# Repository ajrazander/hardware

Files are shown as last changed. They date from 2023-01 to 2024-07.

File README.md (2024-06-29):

# Hardware
Fun designs demonstrating cool aspects of trapped ion quantum computing.

# [How to trap an atom](https://github.com/ajrazander/hardware/tree/main/ion-trap-demo)

Spinning saddle trapped a ping pong ball

This physics demo shows how an individual atom can be "trapped" for experimental study using an [Paul trap](https://en.wikipedia.org/wiki/Trapped_ion_quantum_computer#Paul_trap). State-of-the-art Paul traps are used for [trapped-ion quantum computers](https://en.wikipedia.org/wiki/Trapped_ion_quantum_computer) and [mass spectroscopy](https://en.wikipedia.org/wiki/Quadrupole_ion_trap). This demo is intended to be as inexpensive as possible (including some 3D printed parts).

### Instructions
Read the [build instructions](https://github.com/ajrazander/hardware/blob/main/ion-trap-demo/README.md#build-instructions) for how to assemble the pieces together including some pictures and videos of it working.

### Experiments
Read the [experiments section](https://github.com/ajrazander/hardware/tree/main/ion-trap-demo#experimenting) for ideas to get you thinking and learning.

# [Hands on Qubit](https://github.com/ajrazander/hardware/tree/main/bloch-sphere-demo)

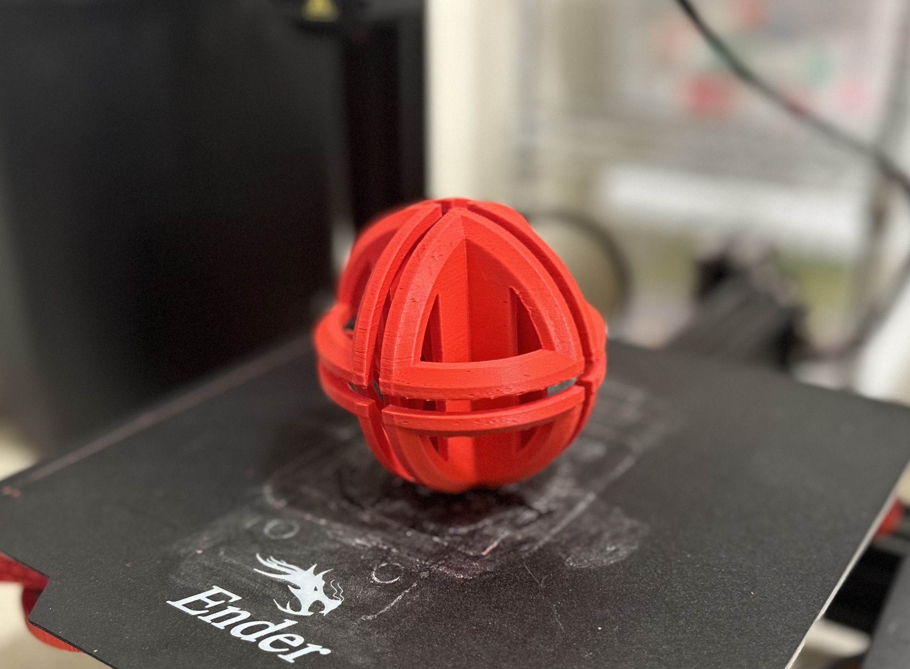
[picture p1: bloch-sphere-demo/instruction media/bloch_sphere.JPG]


Hold a quantum bit---[a qubit](https://en.wikipedia.org/wiki/Qubit)---in your hands and recreate modern experiments with this fully 3D printable [Bloch sphere](https://en.wikipedia.org/wiki/Bloch_sphere) and qubit state vector.

### Instructions
[Read the build instructions](https://github.com/ajrazander/hardware/tree/main/bloch-sphere-demo/README.md#build-instructions) for stl files and assembly.

### Experiments
Coming....

# Want to use these?
I'm happy to see this work be used and shared, so please contact me and request permission before using any of the designs above per the licensing agreement.

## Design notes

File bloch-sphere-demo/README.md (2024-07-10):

# The Bloch Sphere
The [Bloch sphere](https://en.wikipedia.org/wiki/Bloch_sphere) is a visual representation of a two-level quantum system---aka a [qubit](https://en.wikipedia.org/wiki/Qubit). In experiments, qubits do not physically look like the Bloch sphere, but the Bloch sphere can describe the dynamics of a single qubit. Here, you'll have a hands-on learning experience to learn the quantum physics behind qubits, and various techniques used in modern day experiments.

# Build Instructions

### Parts list
* Bloch sphere. A 3D printed Bloch sphere where the qubit vector can glide along set rails. (see designs/bloch_sphere.stl). (June 2024)
* Qubit vector. A 3D printed qubit vector that glides along the Bloch sphere rails. (see designs/qubit_vector.stl) (June 2024)

### Designs
The designs folder holds the 3D printed components which you will need to print:
1. The Bloch sphere. Print with supports.
2. The qubit vector. Printable without supports.

### Assembly

1. Print Bloch sphere (requires supports). Remove support material. Consider sanding where supports were.



2. Print qubit vector.

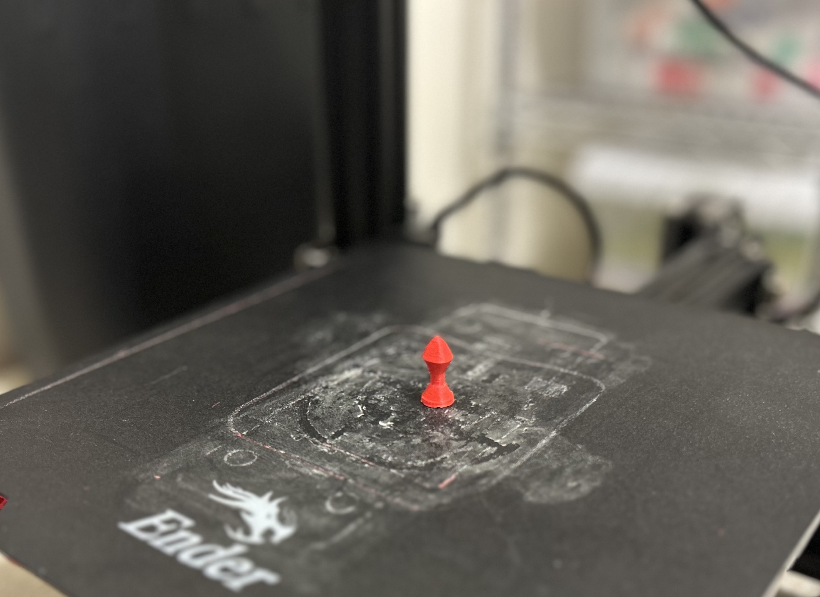
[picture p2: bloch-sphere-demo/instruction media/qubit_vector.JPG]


3. Slip qubit vector into Bloch sphere rails. It’s easiest at an intersection.

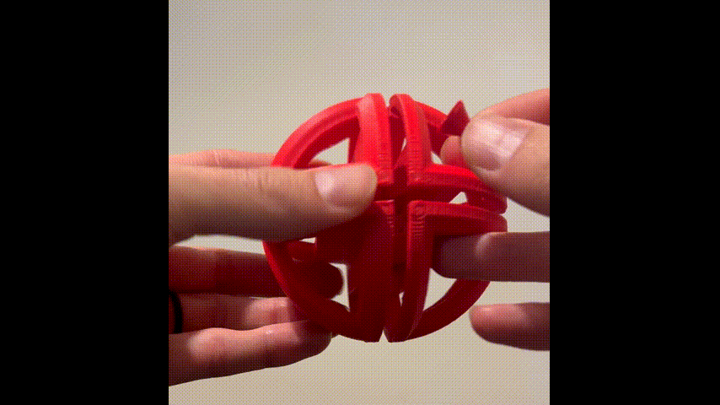
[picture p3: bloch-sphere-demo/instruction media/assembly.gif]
Slip qubit vector into Bloch sphere rail


#  Experimenting
Coming…

### Noncommuting quantum operations

Rubik's cube demonstration. The cube is rotated two different directions. Depending on the order, the yellow side ends up in a different location.

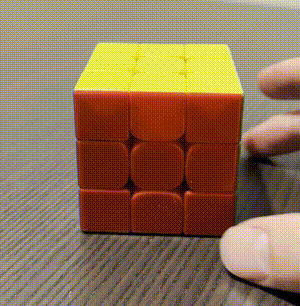
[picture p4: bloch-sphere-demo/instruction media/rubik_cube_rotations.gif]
Rotations on Rubik's cube


Bloch sphere demonstration. The vector is rotated two different directions. Depending on the order, the vector ends up in a different location. This is an example of how the order of quantum operations also matter.

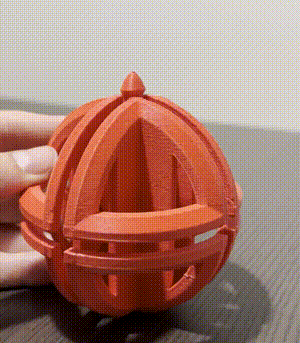
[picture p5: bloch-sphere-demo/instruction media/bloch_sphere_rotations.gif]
Rotations on the Bloch Sphere


# Literature
Coming...

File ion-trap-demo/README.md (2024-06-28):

# The Trapped Atomic Ion
How do you trap one atom? Wolfgang Paul and Hans Dehmelt were awarded [the Nobel Prize](https://www.nobelprize.org/prizes/physics/1989/summary/) for one strategy which is now called [the Paul trap](https://en.wikipedia.org/wiki/Ion_trap) (or RF trap). Here, you'll demonstrate it with a ping pong ball for the ion (a charged atom) and a spinning saddle for the oscillating voltages.

Spinning saddle trapped a ping pong ball

The physics of how an *individual* atom can be "trapped" in a vacuum for experimental study is fascinating. It's also led to a few Noble prizes and dramatically advanced the fields of [atomic, optical, and molecular physics](https://en.wikipedia.org/wiki/Atomic,_molecular,_and_optical_physics) as well as [quantum information](https://en.wikipedia.org/wiki/Quantum_information). This ion trap demo is a simple analogy for how individual atoms are actually trapped in a [linear Paul trap](https://en.wikipedia.org/wiki/Ion_trap#Linear_Paul_Trap).

In Paul traps used for quantum computing, the atom would first be ionized by a laser (or two) at the center of the Paul trap. The atom then has a net positive charge, so we call it an ion. The ion's net charge is pushed by the voltages on the Paul trap's electrodes in such a way that the ion can't escape--hence the ion is "trappped". How the electrode voltages can push on the ion is actually quite limited (see [Earnshaw's theorem](https://en.wikipedia.org/wiki/Earnshaw%27s_theorem)). To get around this limitation, Paul trap electrodes have oscillating (colloquially refered to as rf) voltages and static voltages. *We'll just focus on the oscillating voltages in this demo.* The oscillating voltages make a saddle like shape, but why doesn't the ion just fall off the sides of the saddle and escape? This demo shows how. Gravity and the rotating saddle simulate how the oscillating voltages in a linear Paul trap can trap an ion.

# Build Instructions

### Parts list
This is what and where I purchased each item (if you find something cheaper let me know).
* Housing. A 3D printed container to hold everything together (see designs/box_v4.stl). (Feb 2023)
* Saddle potential. A 3D printed saddle that "traps" the ping pong ball (see designs/saddle_100xy_50z.stl). (Jan 2023)
* ~600 grit sand paper. You want something fine to smooth the saddle. This will dramatically increase the trapping time. (Jan 2023)
* 12V DC motor (you'll want it geared down to the range of a few hundred RPM). Used to spin the saddle. Review the paper under the literature folder to calculate how much speed you may want. 1Hz (60 RPM) seems to be a golden speed for most saddles. I purchased one [online for $15](https://www.amazon.com/gp/product/B072R5G5GR/ref=ppx_yo_dt_b_asin_title_o08_s00?ie=UTF8&th=1) that's probably too beefy but I like the standing geometry (Jan 2023).
* 12V DC motor speed controller. You could make this yourself if you have access to a basic electronics. I purchased [these online for $10](https://www.amazon.com/gp/product/B08HQQR3FQ/ref=ppx_yo_dt_b_asin_title_o01_s01?ie=UTF8&psc=1) (Jan 2023)
* 8 AA battery holder. Used to power the DC motor. I bought it [here for $7](https://www.amazon.com/gp/product/B07WP1CYYW/ref=ppx_yo_dt_b_asin_title_o01_s00?ie=UTF8&psc=1) (Jan 2023)
* 8 AA batteries. (Jan 2023)
* Ping pong ball. The ping pong ball is the "atom" in the trap. I used a standard 40mm size ping pong ball and [purchased a few here for $10](https://www.amazon.com/gp/product/B00V57KP1G/ref=ppx_yo_dt_b_asin_title_o00_s00?ie=UTF8&th=1). (Jan 2023)
* 2 wires. You'll need 2 wires (red and black look cool) to go from the controller to the motor. (Jan 2023)

### Designs
The designs folder holds the 3D printed components which you will need to print:
1. The saddle which sits on top of the motor shaft.
2. The housing that holds all the components together.
The Mathematica file "saddle-design.nb" allows you to export your own custom saddle stl file. (It's suprisingly easy; then use tinkercad to get the DC motor attachment shaft on the saddle).

### Assembly
Order and 3D print the parts. On the speed controller PCB board, secure wire leads that will go to the battery holder and the DC motor (see step 3 for better image).

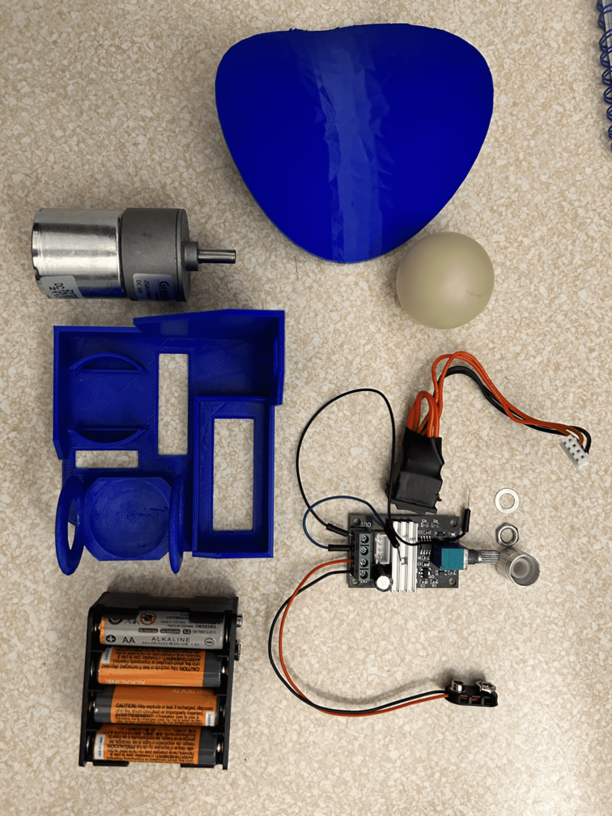
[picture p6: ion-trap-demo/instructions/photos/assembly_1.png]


1. Place batteries in the battery holder and wiggle it into its slot on the 3D printed housing. It should fit snuggly.

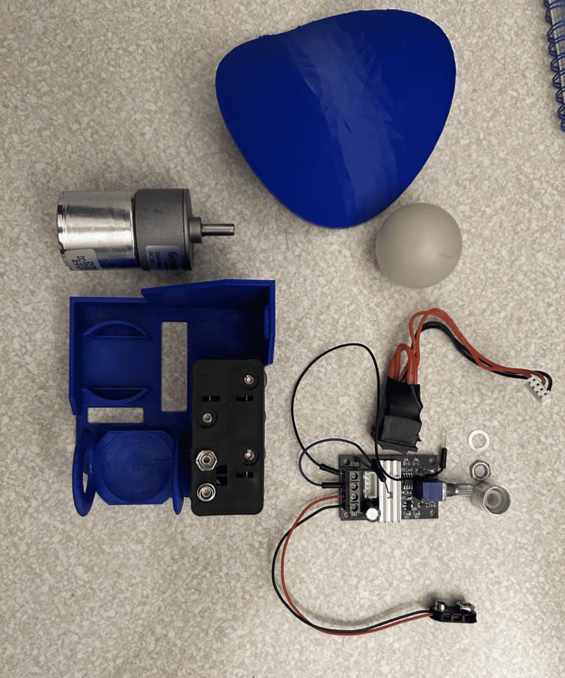
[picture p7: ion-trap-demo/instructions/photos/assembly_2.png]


2. Attach the speed controller board to the 3D printed housing. Disconnect the speed controller’s black switch. Pull the outer knob off the potentiometer and take off the washer and nut under the knob. Push the exposed potentiometer knob through the bottom hole of the 3D printed housing (see image below). This might need some moderate force and wiggling to get the threads through the hole. Reassemble the knob: put the washer back on, tighten the nut, and push the knob back on.

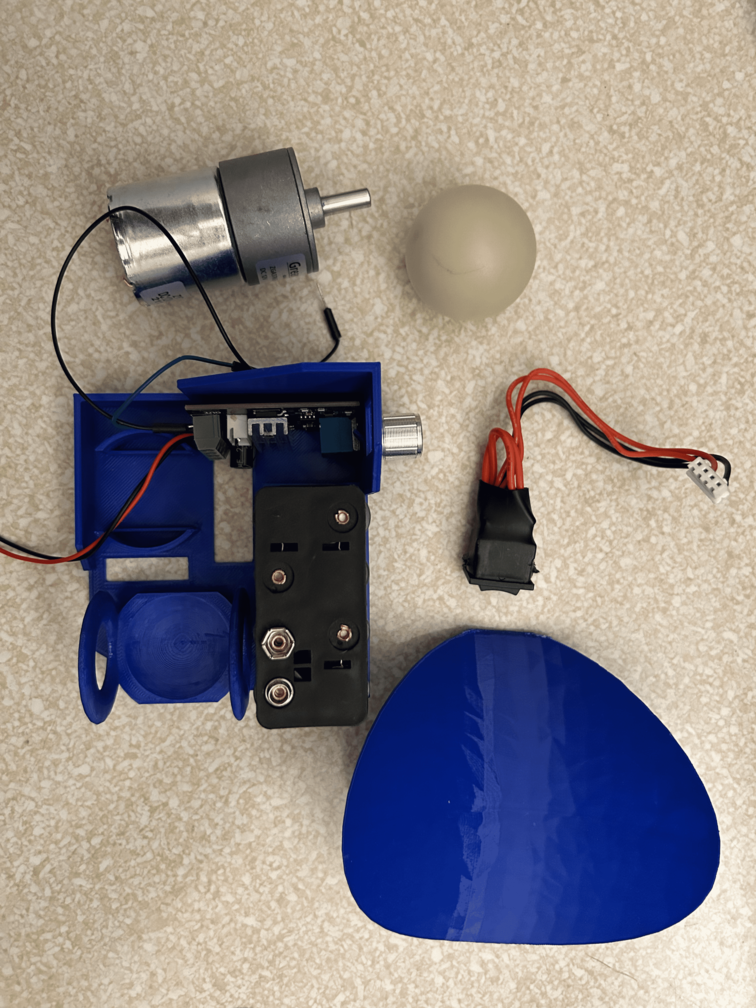
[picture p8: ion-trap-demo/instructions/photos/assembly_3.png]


3. Attach the speed controller power output to the DC motor. It doesn’t matter which lead from the speed controller is connected to the plus or minus lead of the DC motor. Definitely use a more secure connection than shown here (such as soldering on the wires).

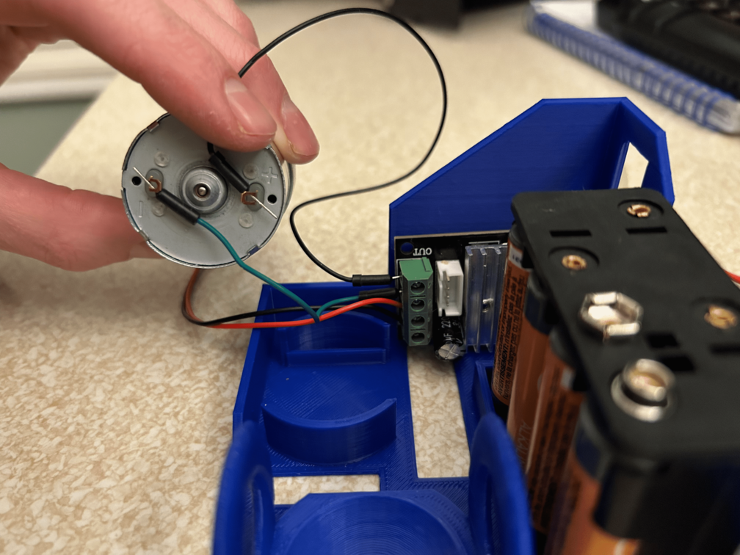
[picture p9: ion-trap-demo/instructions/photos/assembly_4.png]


4. Put the DC motor in the cylindrical base. Be sure the 3D printed parallel rails in the cylinder match with the metal groves at the bottom of the DC motor casing. This stabilizers the motor’s rotation. Confirm the fit by wiggling the DC motor. It should not rotate.

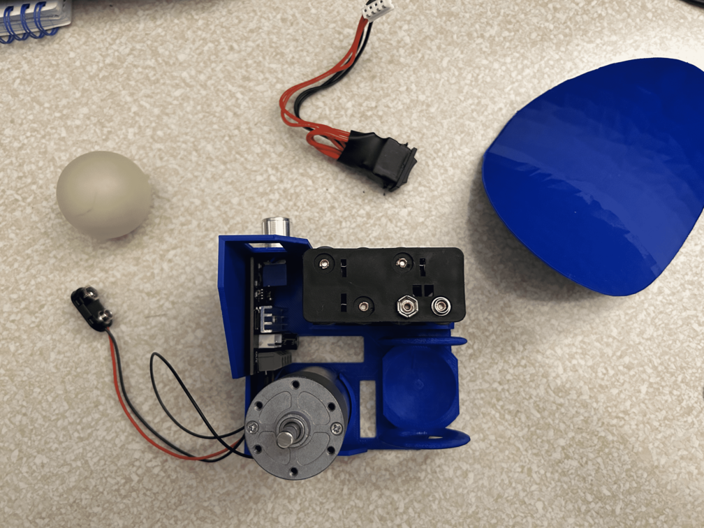
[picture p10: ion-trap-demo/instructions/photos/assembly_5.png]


5. Attach the speed controller switch. Push the white plug from the front rectangular hole of the 3D printed housing to inside the housing by the speed controller. Plug it in to the speed controller. Carefully wiggle and push the black switch into place. It will be a tight fit.

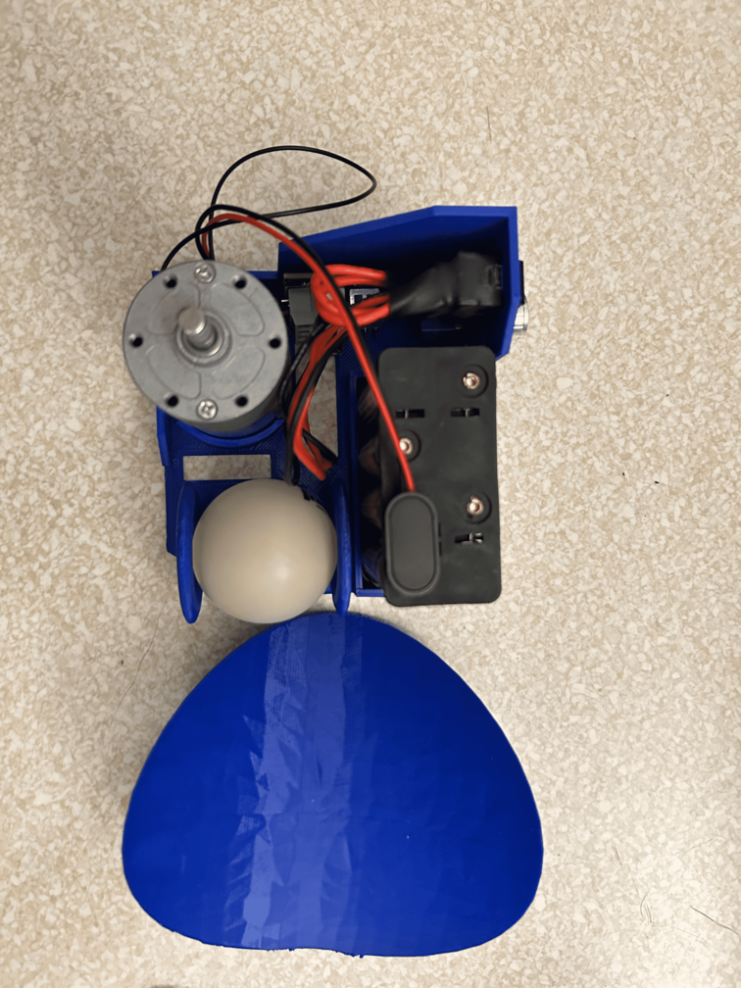
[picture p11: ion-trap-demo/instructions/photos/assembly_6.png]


6. Wrap up. With the speed controller’s switch off. Attach the battery wire leads to the battery holder. Slip the ping pong ball into the socket. Find the flat side of the DC motor shaft and the flat side of the 3D printed saddle’s base and push the saddle on. This might need a bit of force, but should slide on nicely.

7. **You will need to smooth the 3D printed saddle to get good trapped times** (~ minutes of trapping are possible with very smooth saddles). Read more about this under Experimenting point 3.

#  Experimenting
1. Test the DC motor is working as expected. Turn on the dc motor using the controller (without the saddle on the DC motor shaft). Does the DC motor shaft spin? Is the DC motor stable in the cylindrical base? Does varying the speed controller’s potentiometer knob affect the DC motor’s speed? Can you get to the rotational speed you want/calculated for the saddle shape you 3D printed? Troubleshoot accordingly ;).

2. Measure the affect of the saddle’s speed on the trapping time. Start with the saddle spinning at slow speed. Place the ping pong ball in the center of the spinning saddle. If it rolls off, try increasing the speed. If the saddle looks like its flinging the ping pong ball off, try decreasing the speed. Measure the saddle rotation speed and the trapping time. Make a plot.

3. Measure the affect of friction on the trapping time. Measure how long you can keep the ping pong ball trapped in the saddle with different smoothness. Without smoothing the 3D printed saddle, I get about ~10 seconds. After 15 minutes of moderately sanding with wet 600 grit sand paper, I get ~30 seconds. With another 15 minutes of more aggressive sanding (wet sand paper and buff it with a rag so I can’t feel any bumps with my fingers), I can get 60 seconds. Doing more smoothing and adding a dry lubricant (such as non-stick Teflon spray), I’ve seen 10 minutes of continuous trapping.

3. How does the initial condition of the ping pong ball affect the trapping time? Try comparing on-center with off-center starting positions. Try placing the ball in the saddle vs giving the ball a little spin. Try spinning the ping pong ball with vs against the saddle direction. What happens? 

4. Try different balls and saddle shapes! (See designs folder for the Mathematica notebook that can export new saddle stl files)

5. And of course, what’s the longest trapping time you can get and what helped the ball stay trapped for so long?

# Literature
Contains papers I found useful when designing this project as well as the physics this demo is demonstrating. Here are some nice youtube videos demonstrating or explaning the physics in no particular order:
* https://youtu.be/9TH5mFHLmfc
* https://youtu.be/1NBOsELakx4

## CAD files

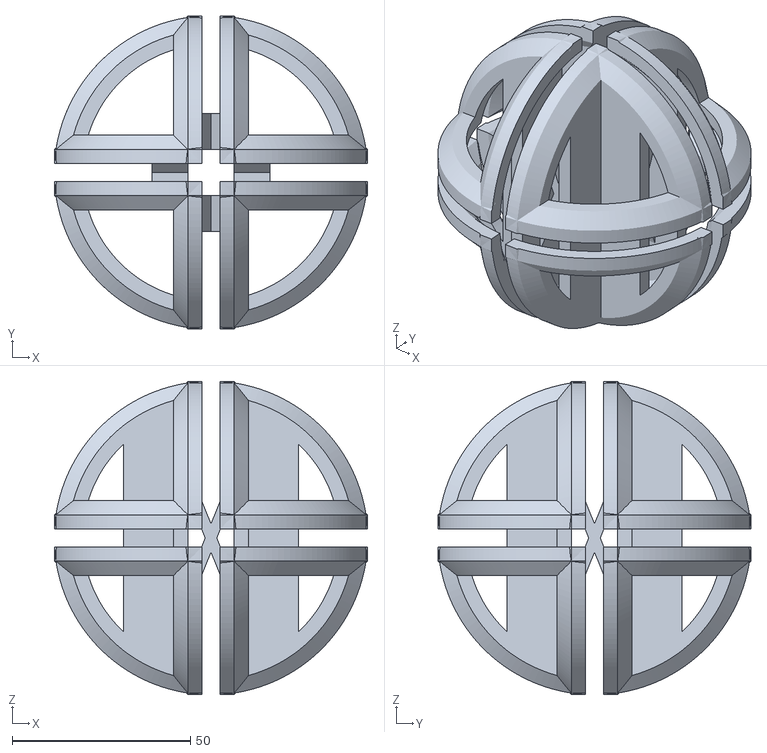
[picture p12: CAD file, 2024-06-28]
bloch-sphere-demo/designs/bloch_sphere.stl
87.9 x 87.9 x 87.9

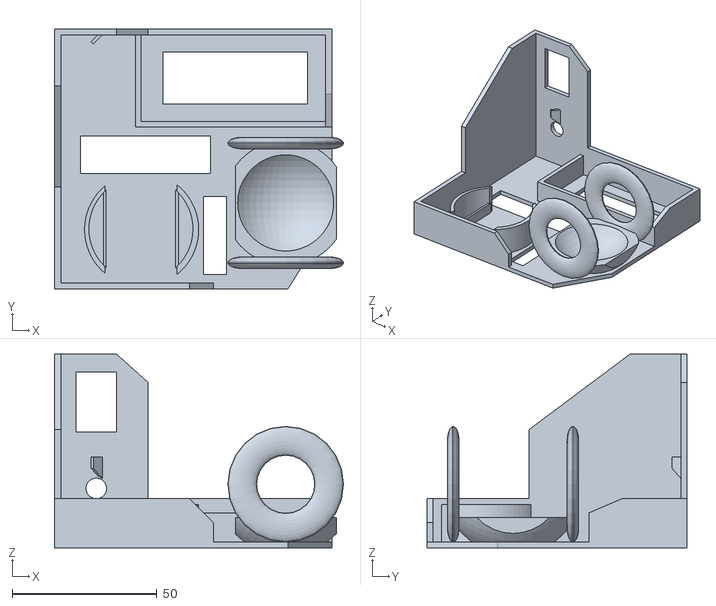
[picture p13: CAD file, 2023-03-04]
ion-trap-demo/designs/box_v4.stl
100.0 x 90.0 x 67.0

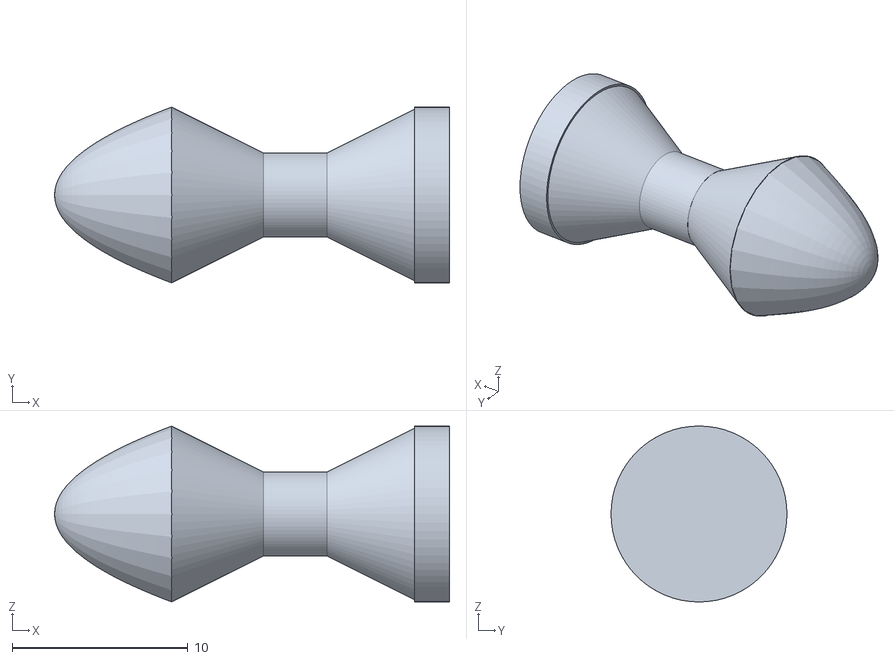
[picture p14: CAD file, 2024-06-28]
bloch-sphere-demo/designs/qubit_vector.stl
22.5 x 10.0 x 10.0

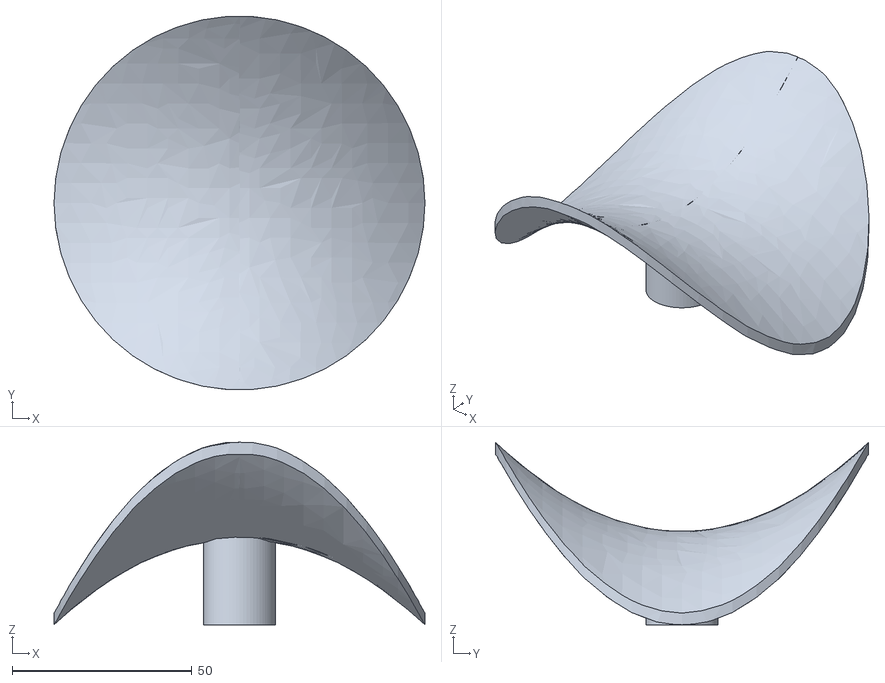
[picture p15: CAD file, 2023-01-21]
ion-trap-demo/designs/saddle_100xy_50z.stl
103.3 x 103.9 x 50.8

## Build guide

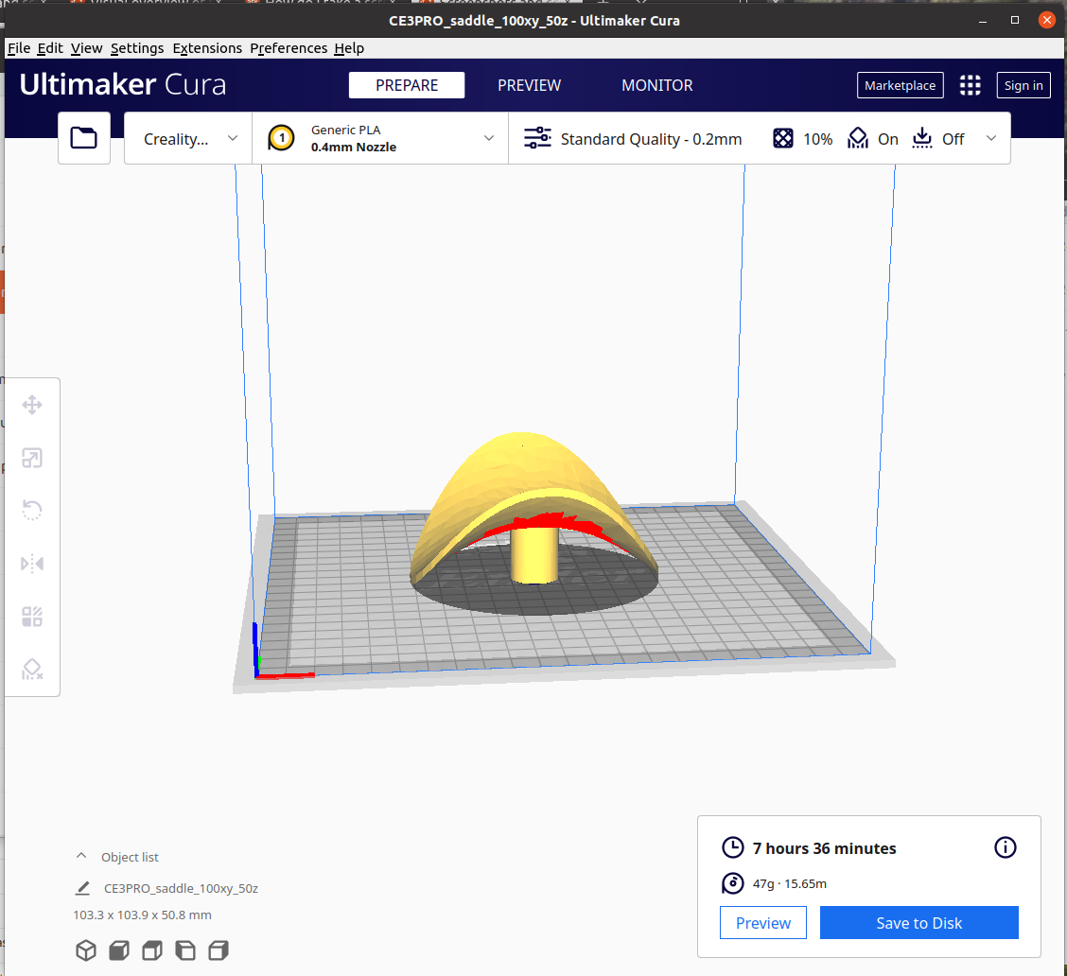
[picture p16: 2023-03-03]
ion-trap-demo/instructions/photos/imported_stl_saddle.png

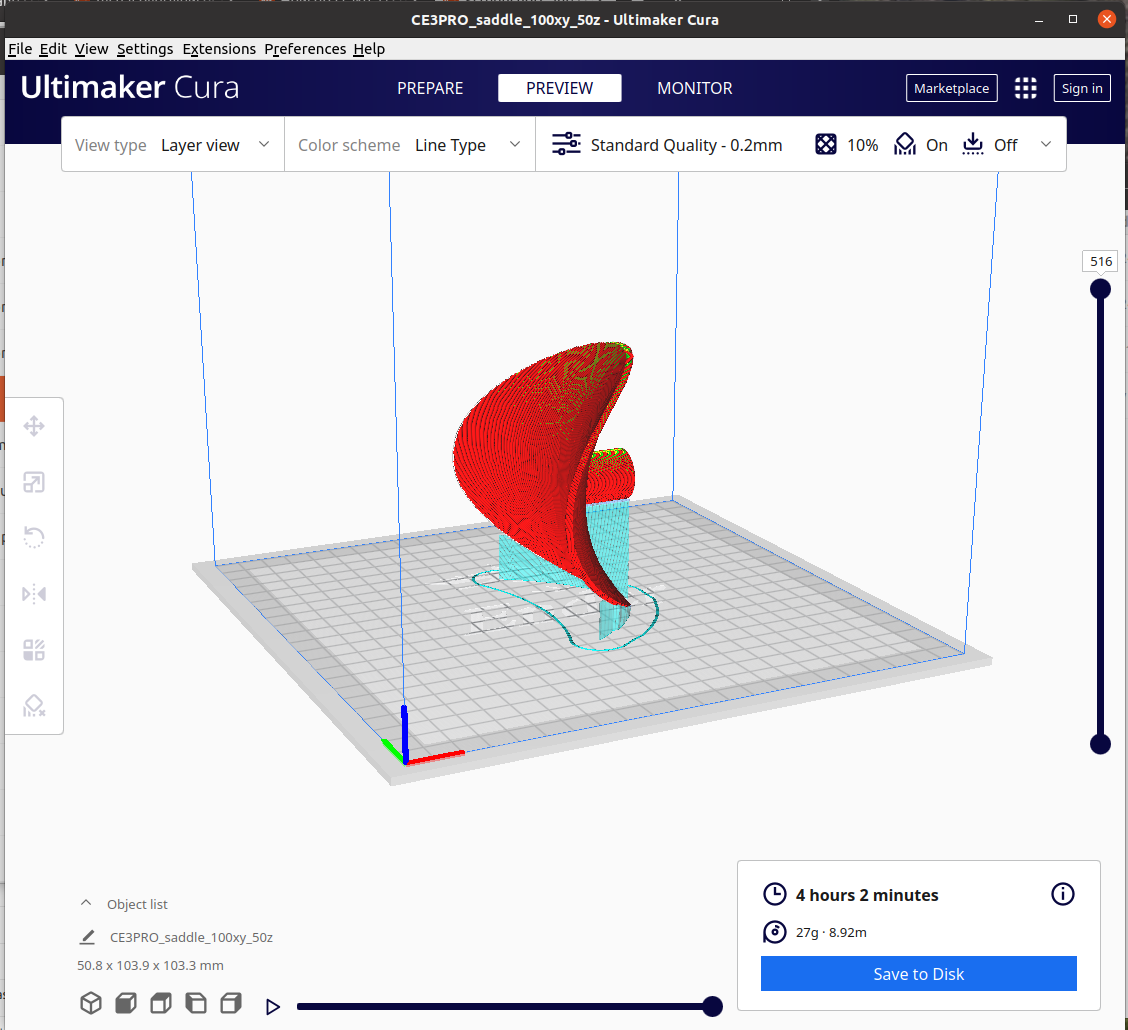
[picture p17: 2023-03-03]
ion-trap-demo/instructions/photos/sliced_saddle.png

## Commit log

2023-01-21 Current 3d designs
    Not quite the final desgins I think. Want to tweak a couple things like letting the LED light through the box
    [box.stl, motor_stand_test.stl, saddle_100xy_50z.stl]
2023-01-21 remove test file; update better box version
    Box more snuggling fits the motor and slims the corners down
    [box.stl, box_v2.stl, motor_stand_test.stl]
2023-01-22 added hole to see LED light
    Also put reflective piece behind the hole to better reflect the light. It looks alright and can be printed without supports (<55 degrees)
    [box_v2.stl, box_v3.stl]
2023-01-28 Update box_v3.stl
    Newer version of box. Still working on holder for ping pong ball
    [box_v3.stl]
2023-03-03 1st draft on assembly instructions
    Need to reduce image size
2023-03-04 Latest housing designs and saddle file
    [box_v4.stl]
2024-06-28 Bloch sphere and vector stl file upload
    [bloch_sphere.stl, qubit_vector.stl]
